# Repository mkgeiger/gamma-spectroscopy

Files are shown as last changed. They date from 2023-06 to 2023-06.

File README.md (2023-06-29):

# Gamma spectroscopy

## Introduction
Sooner or later your fingers will get itchy: once you deal with Geiger counters and with radioactivity, then you just want to try out at some time also gamma spectroscopy. But as a normal electronics hobbyist you usually have a lot of respect for that pure physics stuff with photomultipliers, scintillators and so forth. But once you have dared to cross this barrier, then you ask yourself why not started earlier.

My earlier Geiger counter projects using simple ionization tubes as detectors can only be used to count pulses caused by a passing gamma-ray and deriving the ionizing radiation dose. This project is doing the same, but an additional feature is the capability of measuring also the intensities of the pulses. The intensities of the pulses can be clearly assigned to gamma energies [unit keV]. Most radioactive sources produce gamma rays, which are of various energies and intensities. When these emissions are measured by this spectroscopy project, a gamma-ray energy spectrum can be produced afterwards from the collected data.

As we know now that a simple ionization tube as detector is not capable to measure gamma-ray energies, some other type of gamma-ray detector needs to come into game: a SiPM (Silicon Photo Multiplier) together with a scintillator.

## Scintillator

A scintillator is a material that is excited to glow in the visible range by incoming ionizing particles or radiation. I.e. it releases the absorbed energy in the form of light. A tight coupled photo multiplier is used to measure the sparkling of the emitted light. There exist various types of scintillators for different materials, wavelengths and sensitivities. The widely used NaI(Tl) (thallium-doped sodium iodide) inorganic crystal is also used in this project. The scintillation wavelength of the emitted photons fits to the used blue-sensitive photo multiplier. Incoming high energy radiation, i.e. in our case gamma photons, interact with the NaI(Tl) material and dissipate their kinetic energy to produce electron-hole pairs. The recombination of these electron-hole pairs leads to very short (few microseconds) visible light emissions. The presence of thallium significantly increases the light emission of the crystal and is referred to as an activator for the crystal.

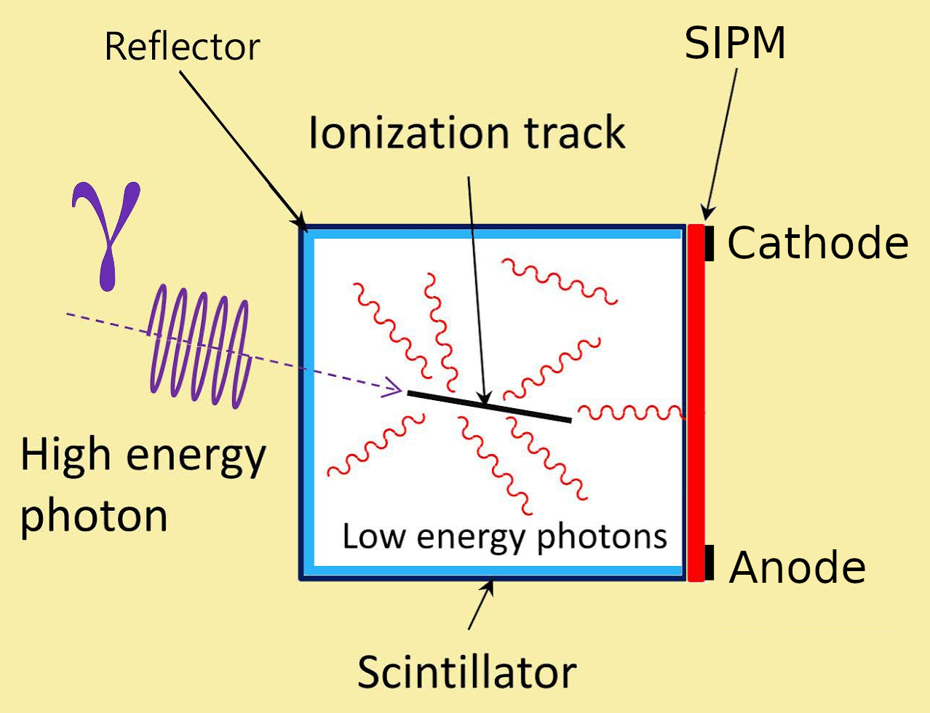
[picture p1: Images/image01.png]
Scintillator With SiPM


The scintillator together with the photo multiplier must be housed in an absolutely light-tight housing so that the ambient light does not falsify the measurements. For this it is best to use some thin aluminum foil and black tape. The size of the used NaI(Tl) crystal is 10x10x30mm. In the following picture you see an example how the scintillator could look like.

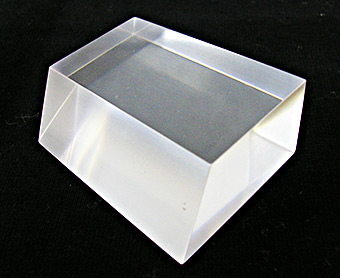
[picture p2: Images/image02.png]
Scintillator NaI(Tl) Crystal


## Photo Multiplier

Typically photomultiplier tubes were used earlier for gamma spectroscopy. Since several years they have been replaced more and more by silicon photomultipliers (SiPMs). The most important benefit of a SiPM is that it doesn't need a high voltage negative power supply of about -1kV like a photomultier tube needs. Therefore also no complicated circuit wiring is required. SiPMs consist of an array of Single Photon Avalanche Diodes (SPAD) which are reverse-biased with sufficient voltage to operate in avalanche mode, enabling each microcell of the array to be sensitive to single photons. 

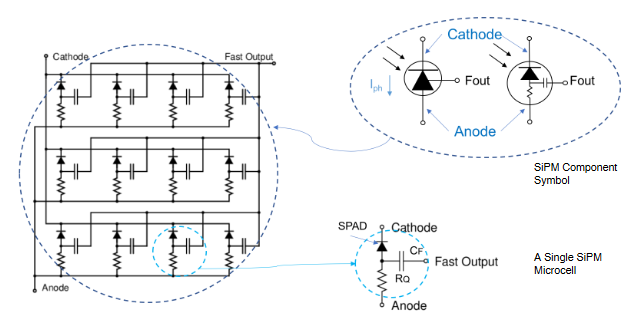
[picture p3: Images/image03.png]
Single Photon Avalanche Diodes


The used SiPM is an [Onsemi MicroFC-30065-SMT](/Datasheets/MICROC-SERIES-D.pdf) device which has ~19000 microcells (SPADs) on an active area of 36mm². See a photo of this SiPM in the following photo.

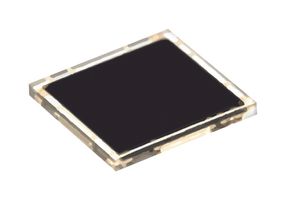
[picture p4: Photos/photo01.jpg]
MicroFC-30065-SMT SiPM


The gain factor of this SiPM is quite high at 3 x 10E6. The reverse-biased voltage (+Vbias) is set to +28V which is available at `TP6` in the schematic of the SIPM module. This bias voltage is also temperature compensated with an NTC (R4) on the feedback loop. The cathode of the SIPM is connected to `TP6` whereas the anode is connected to `TP7` (in reverse direction). Finally the pulses at `TP7` are preamplified by a non-inverting buffer (OPAMP AD8055) and coupled out with 100 Ohm. The full schematic of the SiPM module can be seen in following picture.

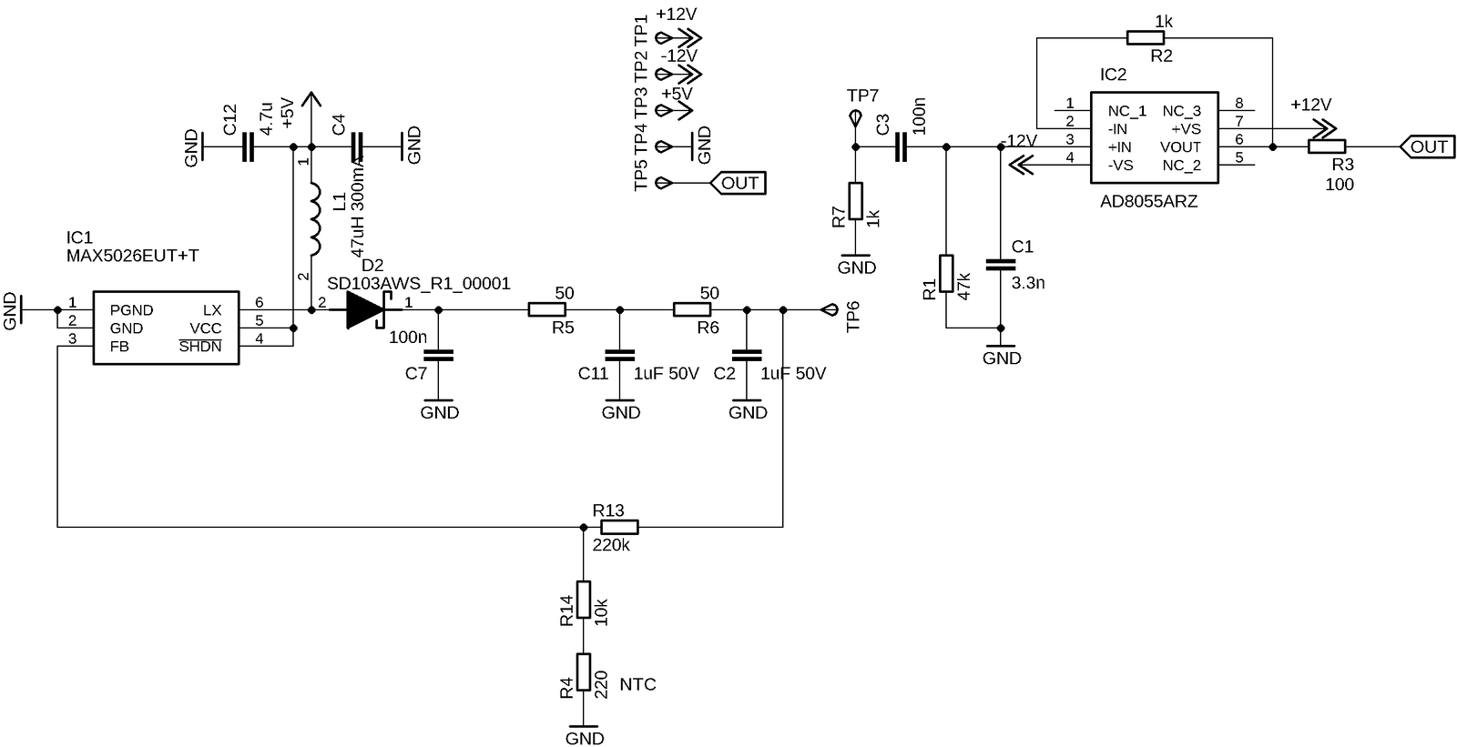
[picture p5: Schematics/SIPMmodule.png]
SiPM Module full schematics


I got the chance to get a fully assembled detector module containing the scintiallator crystal coupled to the SiPM with the biasing and preamp board in light tight housing. In the following see some photos of my detector module.

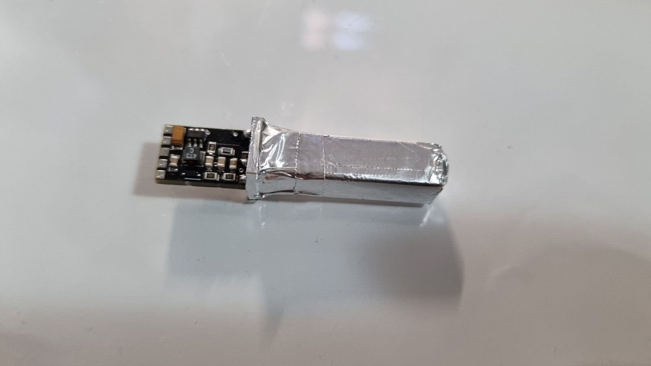
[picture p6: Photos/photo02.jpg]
Scintillator wrapped with aluminium foil and coupled to the SiPM module PCB


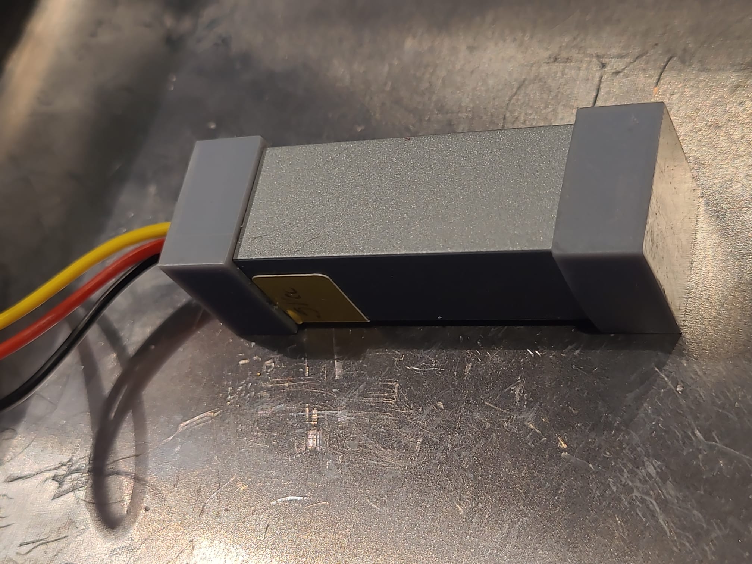
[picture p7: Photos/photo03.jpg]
Completely closed SiPM module with connection cables


The connections of the detector module are:
* Red: +5~9Vcc
* Black: GND
* Yellow: pulse output

## Schematic

The following picture shows the complete schematic including the preamplifier, the sample & hold circuit with the peak detector, the pulse discriminator, the analog-digital converter and the microcontroller. The SiPM module is connected to the `SiPM Module Connector`. Under the given conditions hardware components with the following limitations have been selected:

* as the cicuit operates only with 3.3 Volt the OPAMPs shall operate also with a single power supply of 3.3 Volt.
* rail-to-rail IO shall be supported by the OPAMPs.
* as the pulses generated by the SiPM module are very short (some few micro seconds in total) the bandwidth of the OPAMPs shall be very high (> 100 MHz).
* the used Schottky barrier rectifiers shall have as little forward voltage (VF) as possible (< ~300 mV).
* high quality multi-layer ceramic capacitors for smaller capacitors (<= 100 nF).
* high quality tantals for bigger capacitors (> 1 µF).

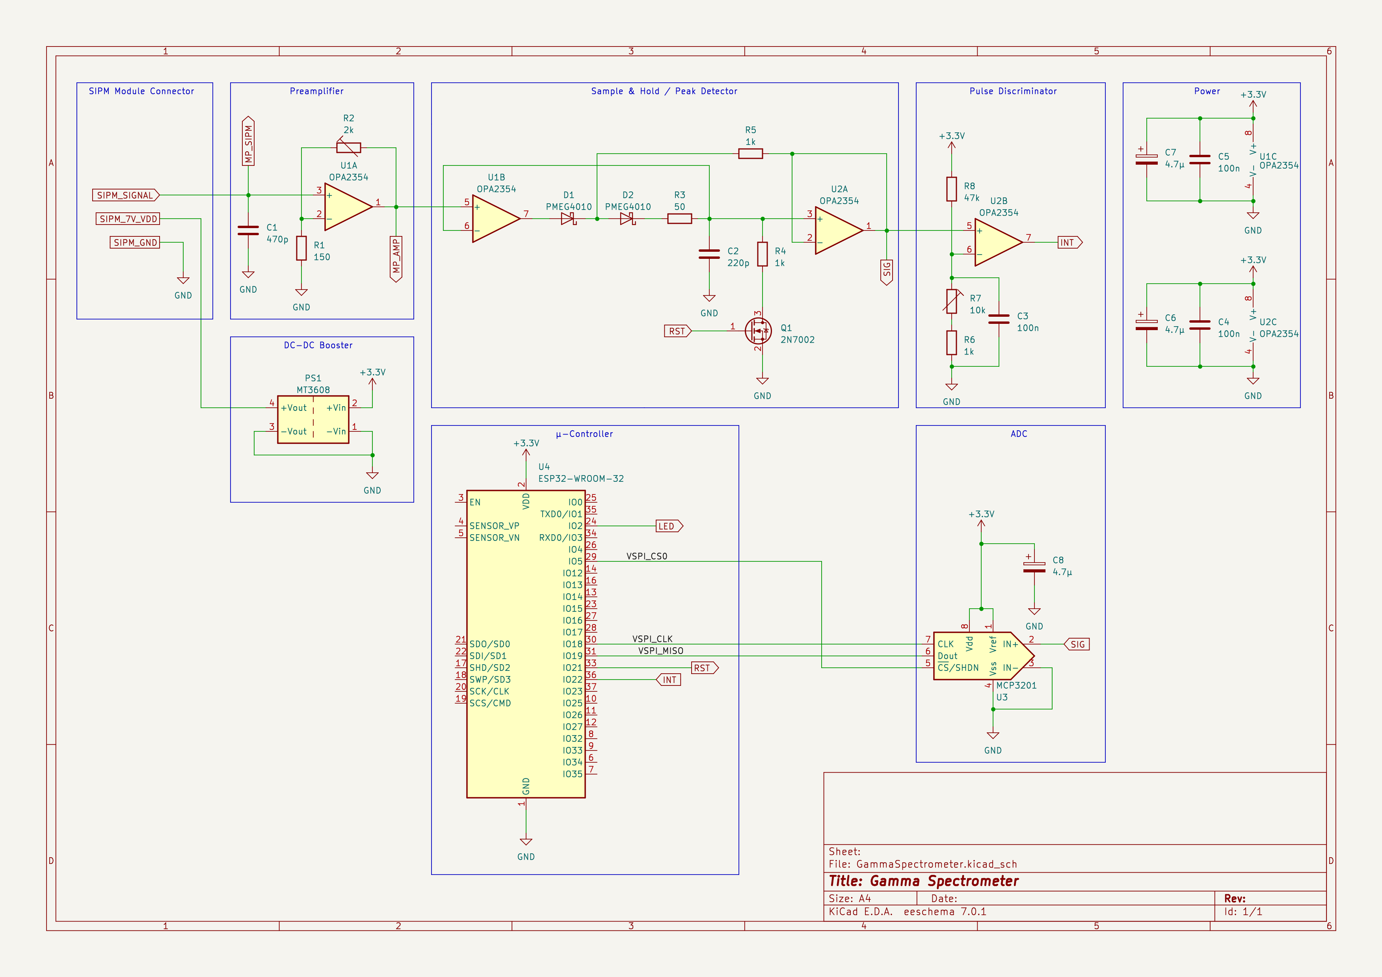
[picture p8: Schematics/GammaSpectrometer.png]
Schematics


### Preamplifier

This circuit operates with 1/2 [TI OPA2354](/Datasheets/OP2354.pdf) in non-inverting amplifying mode. The gain can be configured with a trimmer `R2` in the range 1x - 14x, depending on which range of the gamma spectrum you are interested in. If you want the see the overall gamma spectrum created by this SiPM module (up to 8 MeV) then you would choose a gain factor of 1x. If you want to see the interesting low energy part of the gamma spectrum then you would choose some center position of the trimmer `R2`. The original pulse comming from the SiPM module can be measured at pin `MP_SIPM`. The amplitude of this pulse is equivalent to the energy [keV, MeV] of the gamma photon which caused this pulse. A screenshot taken with the oscilloscope can be seen in the following picture.

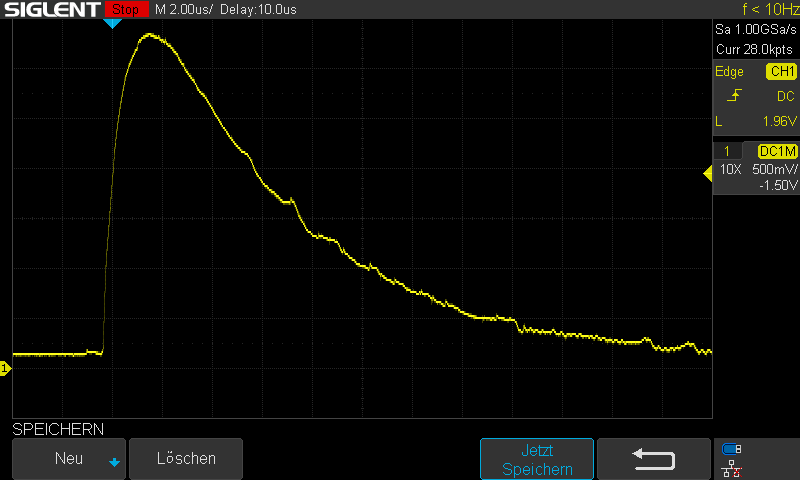
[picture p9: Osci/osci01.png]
Pulse from the SiPM module


The amplified pulse is coupled out at pin `MP_AMP` and fead into the peak detection circuit. The following oscilloscope screenshot shows these pulses as an overlayed picture when having captured the different pulse amplitudes (gamma energies).

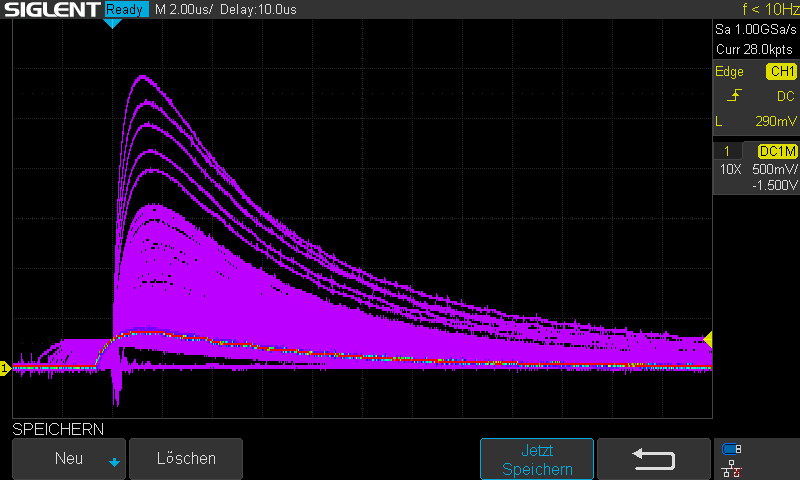
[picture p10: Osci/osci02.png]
Overlayed pulses after the preamplifier


### Peak Detector (Sample & Hold)

This circuit implements an improved and performant peak detection circuit with one [TI OPA2354](/Datasheets/OP2354.pdf), two Schottky diodes [NXP PMEG4010BEA](/Datasheets/PMEG4010BEA_ENG_TDS.pdf) and one N-channel enhancement mode FET [Onsemi 2N7002](/Datasheets/NDS7002A-D.pdf).

It is used to buffer the source of the signal (`MP_AMP`) into the capacitor `C2`. As we can see the circuit is comprised of 2 OPAMPS. A high impedance load is offered by the OPAMP `U1B` to the source. While OPAMP `U2A` performs buffering action in between the load and capacitor `C2`. The voltage at the output side is the similar as the peak of the input signal stored in the capacitor `C2`. Its working is such that, as the input voltage becomes higher than the charge stored on the capacitor `C2`, it charges itself with the new higher value of input signal through the peak detection diode `D2`. However, for a smaller value of the input, the capacitor `C2` sticks to the previous higher value and the peak detection diode `D2` gets reverse biased.

The final piece of the circuit is `R5` and `D1`, which bootstrap the peak detection diode `D2`. Under that condition during the hold period, there can be no leakage through the diode `D2` resulting in a stable voltage at `D2`.

The charge of capacitor `C2` can be resetted/cleared after the hold period actively by the microcontroller at pin `RST`. This is done by discharging `C2` over the conducting FET and `R4`.

The buffered peak signal is coupled out at pin `SIG` and fead into the ADC- and pulse discriminator circuit. The following oscilloscope screenshot shows the buffered peak signal.

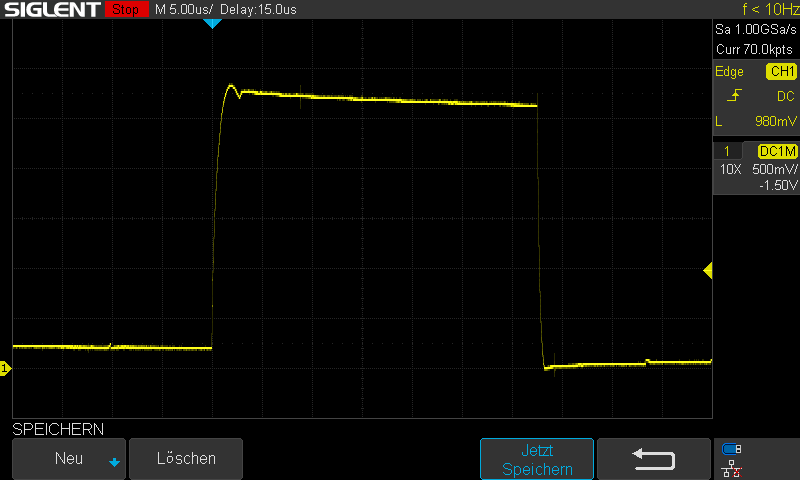
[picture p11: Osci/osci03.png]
Buffered peak signal


### Pulse Diskriminator

This circuit is responsible for setting the trigger level for the microcontroller peak-interrupt. The circuit operates with 1/2 [TI OPA2354](/Datasheets/OP2354.pdf) in non-inverting comparator mode. The trigger level can be configured with a trimmer `R7` in the range ~0.07V - 0.63V. If the voltage of the source signal (`SIG`) is higher than the trigger level the output signal `INT` is set to 'High' (3.3V) as long the voltage of the source signal (`SIG`) doesn't go below the trigger level. Otherwise `INT` is set to 'Low' (0V). This means that during the peak sampling time no other peak-interrupt can be served by the microcontroller. The trigger level must be carefully adjusted to a minimum trigger level to also capture all small energies (peaks) but not too small to also capture noise (false peaks).

The interrupt signal is coupled out at pin `INT` and fead into the microcontroller.

### Analog Digital Converter (ADC)

The internal ADCs of many microcontrollers and as well for the ESP32 microcontroller have some pretty severe [Differencial Nonlinearity (DNL)](https://pico-adc.markomo.me/INL-DNL/#dnl) issues that result in some channels being much more sensitive (wider input range) than the rest.

That was the reason to use the external 12-bit ADC chip [Microchip MCP3201-B](/Datasheets/MCP3201.pdf) with SPI interface, which has a DNL and INL of only a maximum of +-1 LSB. The 12-bit resolution allows a maximum of 4092 energy channels, which is pretty good. The sampling rate of the ADC is about at 50 kHz which means one peak will be sampled in round about 20 µs, which is not very fast, but enough for this project. The 12-bit sample will be read out over SPI by the microcontroller.

### Microcontroller

I decided to take a NodeMCU ESP32 microcontroller board because of its performant cores, easy programming with Arduino IDE in C/C++, WIFI, small form factor, cheap price and a lot of experience from other projects. Following GPIOs are used:

  Signal      | ESP32  | Mode
  ------------|--------|----------------
  LED         | GPIO2  | GPIO output
  VSPI_CS0    | GPIO5  | SPI chip select
  VSPI_CLK    | GPIO18 | SPI clock
  VSPI_MISO   | GPIO19 | SPI data input
  RST         | GPIO21 | GPIO output
  INT         | GPIO22 | GPIO IRQ input
  
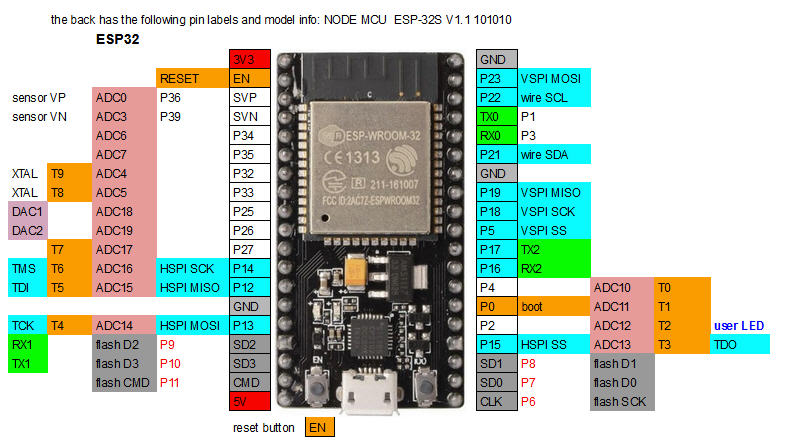
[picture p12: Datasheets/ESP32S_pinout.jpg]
ESP32 NodeMCU
This module can be obtained at Ebay for about 5€. 

## Software
The Software can be found [here](/GammaSpectroMeter).

### Libraries

Following libraries are used by this project:
* [Arduino library for the MCP320x ADC family](https://github.com/labfruits/mcp320x/), a copy of the driver source code comes along with this project
* [WiFiManager](https://github.com/tzapu/WiFiManager)
* [ESPmDNS](https://github.com/espressif/arduino-esp32/tree/master/libraries/ESPmDNS)
* [ESPAsyncWebServer](https://github.com/me-no-dev/ESPAsyncWebServer)
* [ArduinoJson](https://github.com/bblanchon/ArduinoJson)
* [Arduino Time Library](https://github.com/PaulStoffregen/Time)

### Reset of Wifi Manager settings

To reset the Wifi settings (SSID, password) the code line `wm.resetSettings();` needs to be uncommented for one startup. Afterwards the line needs to be commented again and the device starts in Access Point mode (SSID = GammaConnectAP, IP = 192.168.4.1) showing the WifiManager frontendto the user. The new Wifi settings can then be entered.

### Initialization

The MCP320x driver is initialized for the MCP3201 variant with 800 kHz SPI clock because the chip is only powered with 3.3 Volt. Additional configurations for the MCP3201 driver is a reference voltage of 3.3 Volt, the usage of a chip select pin and MSB first transmission. The ISR pin is configured as input triggering the interrupt handler function `handleInterrupt()` on the rising edge.

At the end of initialization the asynchronous webserver is started (which provides the webpages below to the user) and the Multicast DNS protocol allows to connect to the device always with the same hostname with ending `.local` without using the IP address, e.g.:
* http://gamma.local/clear - reset and clear the actual measurement
* http://gamma.local/json - show the measured data in json format which can be downloaded for offline processing and showing
* http://gamma.local/spectrum - show the measured data graphically as a gamma spectrum

### Interrupt

The interrupt caused by gamma pulses is handled in function `handleInterrupt()`. At the beginning of the function at least 3 µs need to be waited until the output signal `SIG` has stabilized and reached its maximum peak. After that this maximum peak is sampled by triggering an ADC conversion. The ADC conversion takes about 20 µs after which the ADC value is read out and the channel corresponding to the sampled ADC value is increased by 1. Each sampled peak - depending on its individual height - will increase one of the 4096 channels. After more and more time the array of channels, which is in fact an array of gamma energies, represents finally a (non callibrated) gamma spectrum. At the end of the function (after the ADC conversion) the peak detection circuit is reset by asserting the signal `RST` for at least 1 µs.

### Data Export

The webserver provides all 4096 channel counters as a JSON formatted stream. This webpage can be displayed in any webbrowser by typing http://gamma.local/json. The displayed JSON stream can be downloaded as a JSON file for further offline processing (e.g. with the Python script). The JSON file contains in the header beside the 4096 channel counters also the elapsed time of the current measurement, the total number of events (peaks) in the current measurement and the average of counts (peaks) per minute. The following screenshot shows an example:

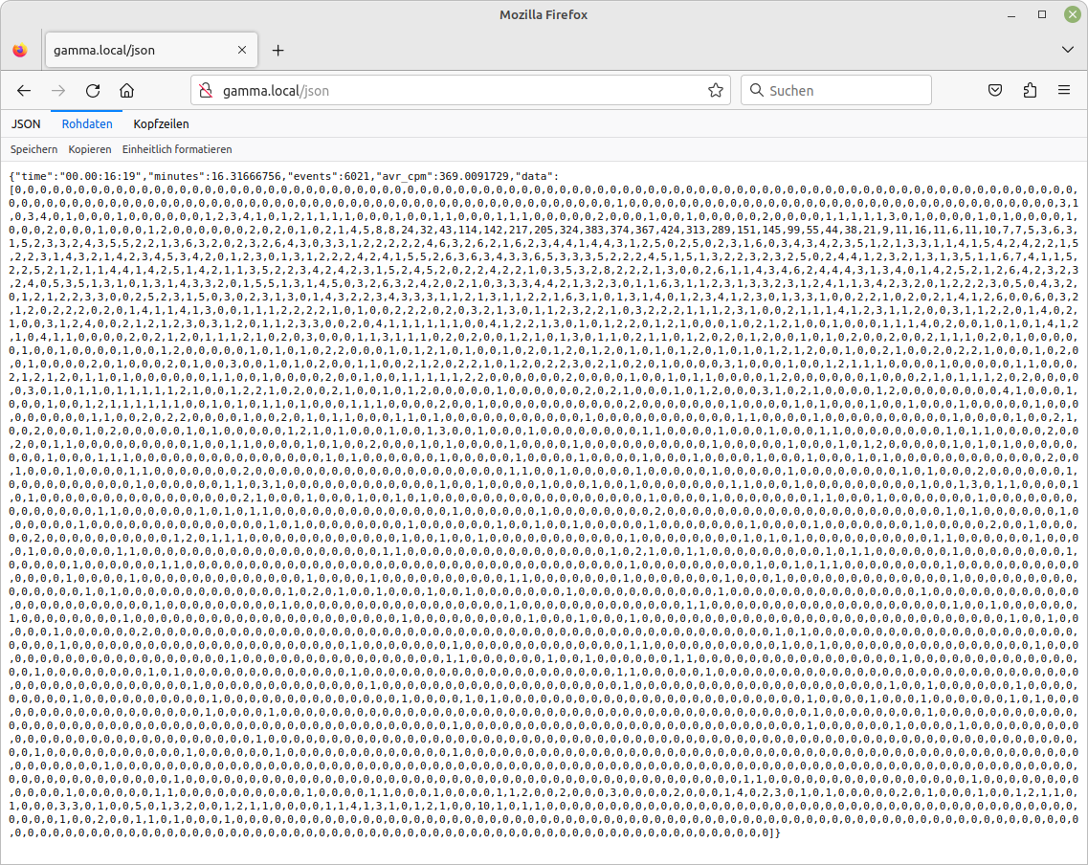
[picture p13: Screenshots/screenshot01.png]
JSON stream


### Visualization

The webserver provides also a visualization of the captured data. This webpage can be displayed in any webbrowser by typing http://gamma.local/spectrum. All channel counters are normalized by the elapsed time (unit: cpm, counts per minute) and are on the y-axis, whereas the channels [0 .. 4095] are on the x-axis. This gives you a gamma spectrum. An embedded javascript helps for visualization the spectrum in a Google line chart. The javascript produces also a second smoothed curve (red) which is generated by a kind of 2-way low pass filter. Beside this some useful information is shown in the heading of the webpage, e.g. the elapsed time of the current measurement, the total number of events (peaks) in the current measurement and the average of counts (peaks) per minute. The following screenshot shows an example:

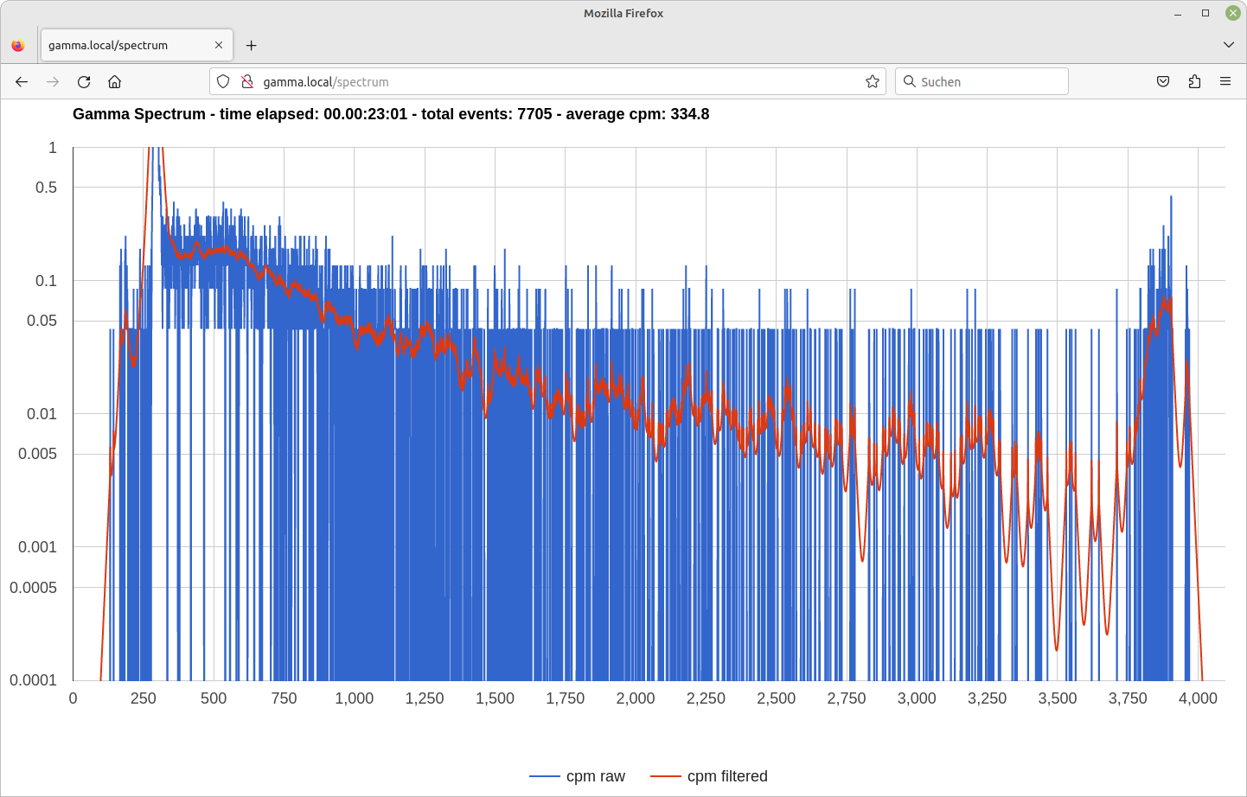
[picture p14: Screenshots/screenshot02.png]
Spectrum


### Offline processing

The exported JSON files can be processed offline. For that I have written a small Python tool (call: python3 [plot_gamma_spectrum.py](/Scripts/plot_gamma_spectrum.py) <json_file>) to better visualize the gamma spectrum. Difference to the webpage visualization is now that the x-axis is converted from channels into calibrated gamma energies [keV]. The calibration (mapping to the corresponding channel) is done in the script for 0 keV, the CS-137 and the K-40 isotope. An energy table for the most common radio isotopes (whhich are emitting at least gamma-rays) is included in the script to show vertical lines at those gamma energies. The maximum visible range for the x-axis can be configured to cut off all higher energies, whose corresponding peak voltages were beyond 3.3 Volt and where the ADC input was saturated. Otherwise you would see a very high irritating peak at the end of the x-axis (which is in fact the sum of all higher energies where the ADC input was saturated). The script contains the same 2-way low pass filter as implemented on the device to show also a smoothed curve. The Python script uses following libraries:
* pandas: for JSON file import
* mathplotlib: for the graphics and chart stuff
* mplcursors: for interactive data selection cursor

The following screenshot shows a spectrum of Lutetium(III) oxide (LU²O³), which has been under measurement for about 21 hours. The 2 typical gamma peaks of the contained isotope LU-176 can be seen at 202 keV and 307 keV.

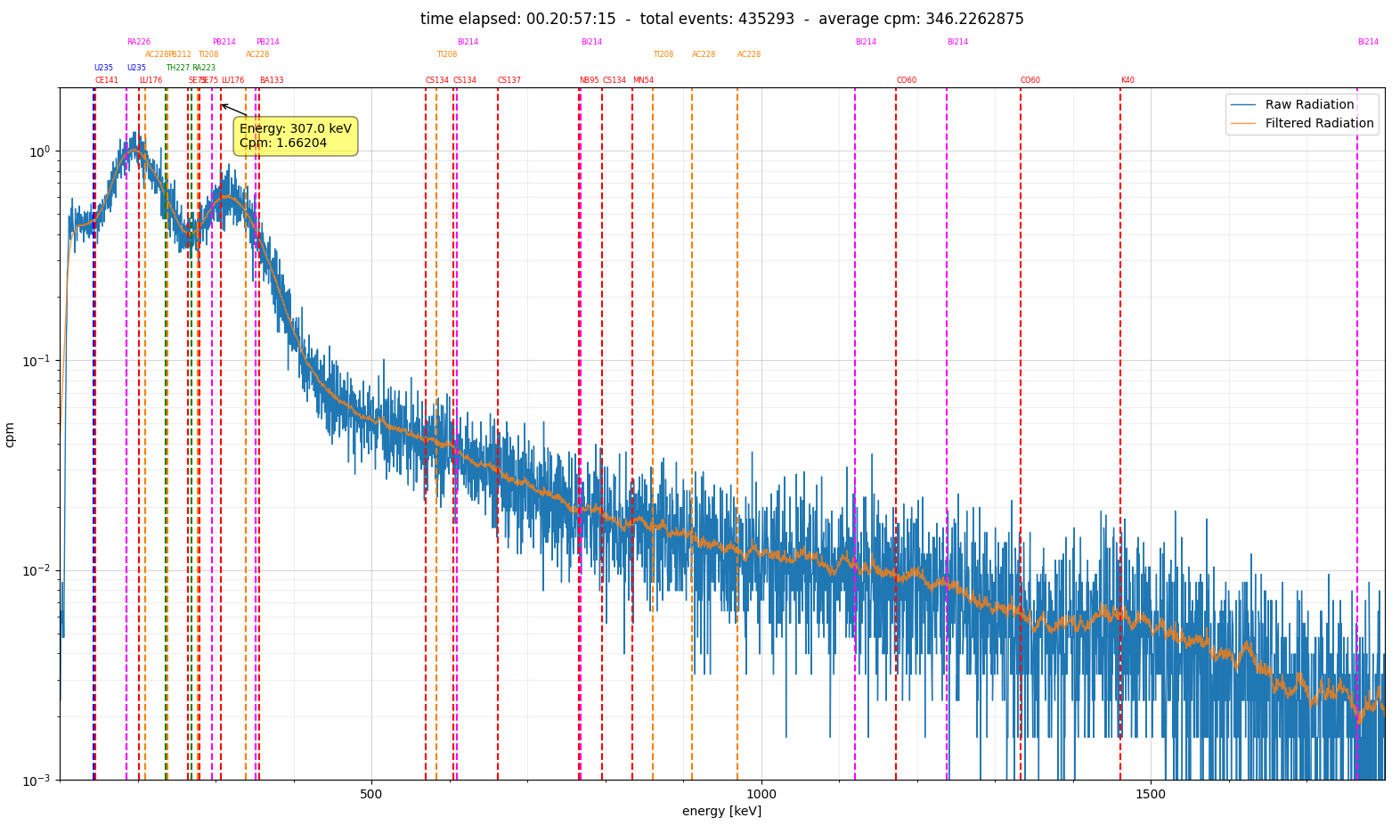
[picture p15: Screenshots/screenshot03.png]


Some other examples for gamma specra (JSON files) can be found in folder [Spectra](/Spectra/).

## Photos

The PCB containing the ESP32, the analog circuit with the OPAMPs, the DC-DC step up boost converter for the SiPM bias voltage:
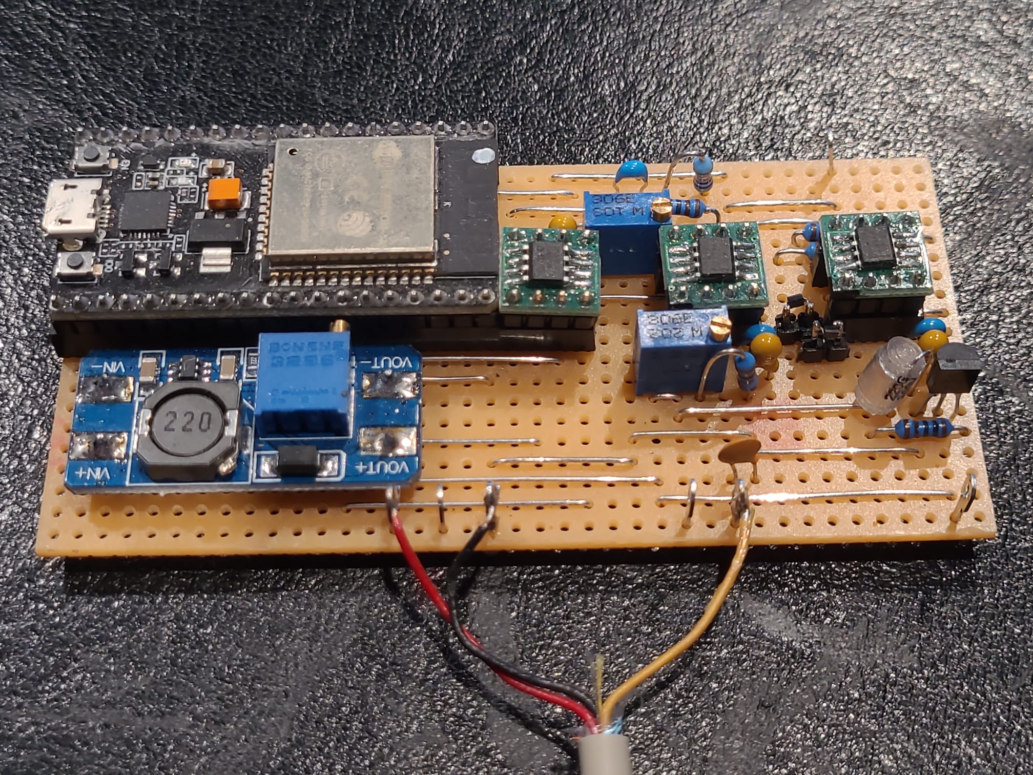
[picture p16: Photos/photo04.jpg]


The measurement metal box is shielded with 1.25mm thick lead. This reduces the background gamma radiation by about 25% and increases the signal to noise ratio. Only the SiPM detection module is inside the box:
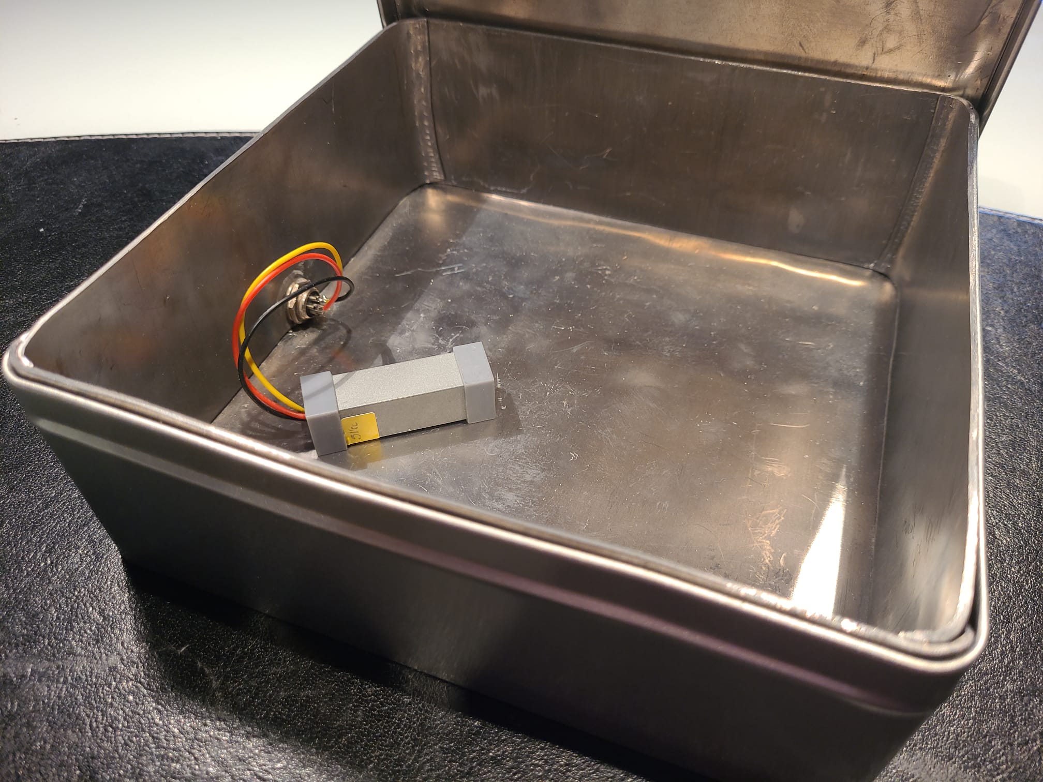
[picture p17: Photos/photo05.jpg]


The PCB connected to shielded box:
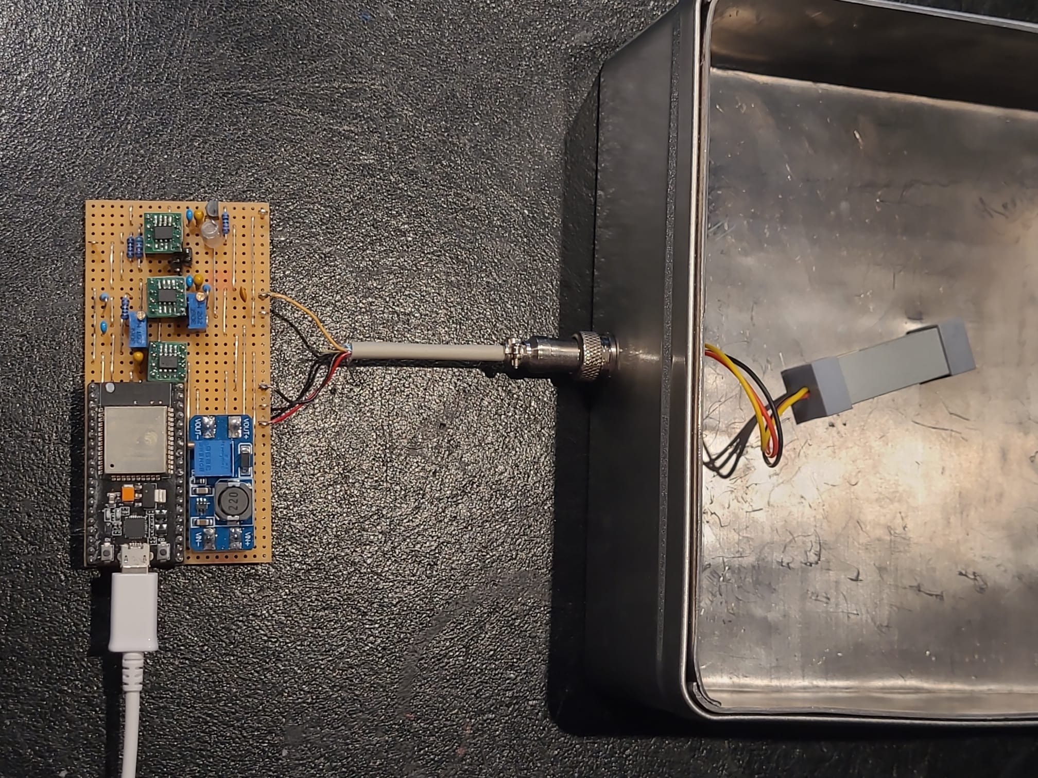
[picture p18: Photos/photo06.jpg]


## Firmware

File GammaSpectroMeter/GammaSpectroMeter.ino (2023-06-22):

#include <SPI.h>
#include "Mcp320x.h"
#include <WiFiManager.h>
#include <ESPmDNS.h>
#include <ESPAsyncWebServer.h>
#include <ArduinoJson.h>
#include <TimeLib.h>

// access point
#define AP_NAME           "GammaConnectAP"
#define AP_TIMEOUT        60

// GPIOs
#define LED_PIN           17   // 2 for onboard blue LED
#define INT_PIN           22   // event capture
#define RST_PIN           21   // reset sample & hold
#define VSPI_CS_PIN        5   // SPI chip select

// ADC MCP3201-B
#define ADC_BITS          12                 // resolution
#define ADC_CHANNELS      (1ul << ADC_BITS)
#define ADC_VREF          3300               // 3.3V Vref
#define ADC_CLK           800000             // SPI clock 800kHz

// variables
static volatile uint32_t  events = 0ul;
static uint32_t           last_timestamp = 0ul;
static uint16_t           spectrum[ADC_CHANNELS] = {0u};
static uint8_t            led_time = 0u;
static char               timebuf[20];
static double             minutes;
static MCP3201            adc(ADC_VREF, VSPI_CS_PIN);
static WiFiManager        wifiManager;
static AsyncWebServer     server(80);

// WiFi events
void WiFiEvent(WiFiEvent_t event)
{
    Serial.printf("WiFi-event: %d\n", event);

    switch (event)
    {
    case SYSTEM_EVENT_STA_GOT_IP:
        Serial.println("WiFi connected.");
        Serial.print("IP address: ");
        Serial.println(WiFi.localIP());
        break;
    case SYSTEM_EVENT_STA_DISCONNECTED:
        Serial.println("WiFi lost connection.");
        break;
    default:
        break;
    }
}

// time elapsed since reset
static void timeSinceReset(char *timebuf)
{
    uint32_t seconds = (millis() - last_timestamp) / 1000;
    uint32_t minutes = seconds / 60;
    uint32_t hours = minutes / 60;
    uint32_t days = hours / 24;

    seconds %= 60;
    minutes %= 60;
    hours %= 24;
    sprintf(timebuf, "%02d.%02d:%02d:%02d\0", days, hours, minutes, seconds);
}

// minutes since reset
static float minutesSinceReset(void)
{
    uint32_t seconds = (millis() - last_timestamp) / 1000;
    return ((float)seconds / 60.0);
}

// reset sample and hold circuit
static void resetSampleHold(void)
{
    digitalWrite(RST_PIN, HIGH);
    delayMicroseconds(1);  // discharge for 1 µs, actually takes 2 µs - enough for a discharge
    digitalWrite(RST_PIN, LOW);
}

// event capture ISR
void IRAM_ATTR handleInterrupt(void)
{
    uint16_t raw;

    // turn on LED for at least 100 ms
    digitalWrite(LED_PIN, HIGH);
    led_time = 200u;

    // wait at least 3 µs to allow the sample/hold circuit to stabilize
    delayMicroseconds(3);

    // 1 measurements takes about 25 µs
    raw = adc.read(MCP3201::Channel::SINGLE_0);

    // update the spectrum
    spectrum[raw] ++;

    // reset the Sample & Hld at the end of ISR
    resetSampleHold();

    // increase total amount of events
    events ++;
}

void setup(void)
{ 
    // set pin modes and states
    pinMode(LED_PIN, OUTPUT);
    digitalWrite(LED_PIN, LOW);

    pinMode(RST_PIN, OUTPUT);
    digitalWrite(RST_PIN, LOW);

    pinMode(INT_PIN, INPUT);

    pinMode(VSPI_CS_PIN, OUTPUT);
    digitalWrite(VSPI_CS_PIN, HIGH);

    // initialize UART
    Serial.begin(115200);

    // initialize SPI interface for MCP3201
    SPISettings settings(ADC_CLK, MSBFIRST, SPI_MODE0);
    SPI.begin();
    SPI.beginTransaction(settings);

    // ISR initialization
    resetSampleHold();
    attachInterrupt(digitalPinToInterrupt(INT_PIN), handleInterrupt, RISING);

    // Wifi initialization
    WiFi.mode(WIFI_STA);
    WiFi.setSleep(false);
    WiFi.setAutoReconnect(true);
    WiFi.onEvent(WiFiEvent);

    //wm.resetSettings();

    wifiManager.setConfigPortalBlocking(false);
    wifiManager.setConfigPortalTimeout(AP_TIMEOUT);

    if(!wifiManager.autoConnect(AP_NAME))
    {
        Serial.println("Configportal running");
    }
    else
    {
        // access the webserver with URL "gamma.local"
        if (!MDNS.begin("gamma"))
        {
            Serial.println("Error setting up MDNS responder!");
            while(1)
            {
                delay(1000);
            }
        }

        // initialize webserver URLs
        server.on("/clear", HTTP_GET, [](AsyncWebServerRequest *request) {
            AsyncResponseStream *response = request->beginResponseStream("text/html");

            for (int i = 0; i < ADC_CHANNELS; i ++)
            {
                spectrum[i] = 0u;
            }
            last_timestamp = millis();
            events = 0ul;

            response->println("<html>");
            response->println("  <head>"); 
            response->println("  </head>"); 
            response->println("  <body>");
            response->println("    <p>Current measurement data has been cleared!</p>");
            response->println("  </body>");
            response->println("</html>");
            request->send(response);
        });

        server.on("/json", HTTP_GET, [](AsyncWebServerRequest *request) {
            AsyncResponseStream *response = request->beginResponseStream("application/json");
            DynamicJsonDocument json(70000);

            timeSinceReset(timebuf);
            minutes = minutesSinceReset();

            json["time"] = timebuf;
            json["minutes"] = minutes;
            json["events"] = events;
            json["avr_cpm"] = events / minutes;
            for (int i = 0; i < ADC_CHANNELS; i ++)
            { 
                json["data"][i] = spectrum[i];
            }

            serializeJson(json, *response);
            request->send(response);
        });

        server.on("/spectrum", HTTP_GET, [](AsyncWebServerRequest *request) {
            AsyncResponseStream *response = request->beginResponseStream("text/html");

            timeSinceReset(timebuf);

            response->println("<html>");
            response->println("  <head>");
            response->println("    <script type=\"text/javascript\" src=\"https://www.gstatic.com/charts/loader.js\"></script>");
            response->println("    <script type=\"text/javascript\">");

            response->println("      google.charts.load('current', {'packages':['corechart']});");
            response->println("      google.charts.setOnLoadCallback(drawChart);");

            response->println("      function lowPassZeroPhase(input, output, smoothing) {");
            response->println("        var temp = new Array(input.length);");
            response->println("        var value;");
            response->println("        var in_len = input.length;");
            response->println("        value = input[0];");
            response->println("        for (var i = 1; i < in_len; i++) {");
            response->println("          var currentValue = input[i];");
            response->println("          value += (currentValue - value) / smoothing;");
            response->println("          temp[i] = value;");
            response->println("        }");
            response->println("        value = input[in_len - 1];");
            response->println("        for (var i = 1; i < in_len; i++) {");
            response->println("          var currentValue = input[in_len - 1 - i];");
            response->println("          value += (currentValue - value) / smoothing;");
            response->println("          output[in_len - 1 - i] = (temp[in_len - 1 - i] + value) / 2.0;");
            response->println("        }");
            response->println("      }");

            response->println("      function drawChart() {");
            response->print  ("        var count_raw = [");

            minutes = minutesSinceReset();
            for (int i = 0; i < ADC_CHANNELS; i ++)
            {
                response->printf("%d, ", spectrum[i]);
            }

            response->println("          ];");
            response->println("        var cpm_raw = new Array(count_raw.length);");
            response->println("        var cpm_filt = new Array(count_raw.length);");

            response->printf ("        for(i = 0; i < %d; i++) {\n", ADC_CHANNELS);
            response->printf ("          cpm_raw[i] = count_raw[i] / %.2f;\n", minutes);
            response->println("        }");

            response->println("        lowPassZeroPhase(cpm_raw, cpm_filt, 10);");

            response->println("        var data = new google.visualization.DataTable();");
            response->println("        data.addColumn('number', 'channel');");
            response->println("        data.addColumn('number', 'cpm raw');");
            response->println("        data.addColumn('number', 'cpm filtered');");

            response->printf ("        for(i = 0; i < %d; i++) {\n", ADC_CHANNELS);
            response->println("          data.addRow([i, cpm_raw[i], cpm_filt[i]]);");
            response->println("        }");

            response->println("        var options = {");
            response->printf ("          title: 'Gamma Spectrum  -  time elapsed: %s  -  total events: %d  -  average cpm: %.1f',\n", timebuf, events, events / minutes);
            response->println("          curveType: 'none',");
            response->println("          width: 2000,");
            response->println("          height: 1000,");
            response->println("          vAxis: { scaleType: 'log', viewWindow: { min: 0.0001, max: 1}},");
            response->println("          legend: { position: 'bottom' }");
            response->println("        };");

            response->println("        var chart = new google.visualization.LineChart(document.getElementById('gamma_spectrum'));");
            response->println("        chart.draw(data, options);");
            response->println("      }");

            response->println("    </script>");
            response->println("  </head>"); 
            response->println("  <body>");
            response->println("    <div id=\"gamma_spectrum\" style=\"width: 2000px; height: 1000px\"></div>");
            response->println("    <a href=\"/clear\"\"><button>Clear Measurement</button></a>");
            response->println("  </body>");
            response->println("</html>");
            request->send(response);
            yield();
        });

        // start the webserver
        server.begin();

        // add service to MDNS-SD
        MDNS.addService("http", "tcp", 80);
    }
}

void loop(void)
{
    static uint32_t last_exec = 0ul;

    // process wifimanager when in non-blocking mode
    wifiManager.process();

    // reset sample & hold and LED handling
    if (micros() - last_exec >= 500ul)
    {
        // reset Sample & Hold every 500 µs
        resetSampleHold();

        // switch off LED after 100 ms
        if (led_time > 0u)
        {
          led_time --;
        }
        if (led_time == 0u)
        {
          digitalWrite(LED_PIN, LOW);
        }

        last_exec = micros();
    }

    yield();
}

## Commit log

2023-06-15 Photos for assembled modules
2023-06-15 Schematics for the complete circuit
2023-06-20 Peak detection circuit description added
2023-06-22 microcontoller pinout of NodeMCU ESP32 added
2023-06-22 some example spectra captured with this device
2023-06-22 Kicad schematic added
    [GammaSpectrometer.kicad_sch]
